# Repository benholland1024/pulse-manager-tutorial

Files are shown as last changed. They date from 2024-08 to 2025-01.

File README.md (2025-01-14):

<h1 align="center"> 🫀 Pulse Manager Tutorial</h1>

<h4 align="center">A description of how to recreate the hardware needed to use the <a href="https://github.com/benholland1024/pulse-manager">pulse-manager</a> software.</h4>

<br/><hr/><br/>

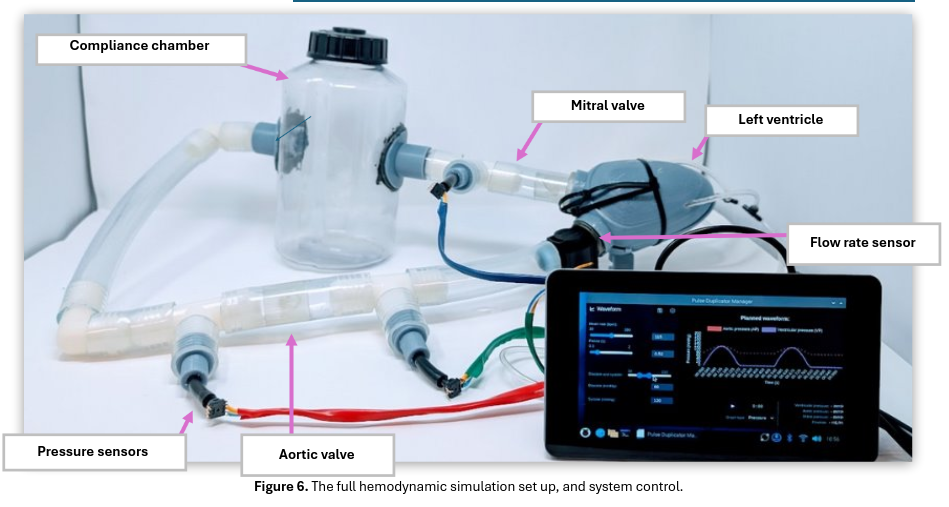
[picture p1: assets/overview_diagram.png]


<h2>Contents</h2>

 1. <a href="#supplies">**Required tools and supplies**</a>
 2. <a href="#cardiovascular-model">**The cardiovascular model**</a>
    - 2.1. Print the heart
    - 2.2. Print the heart casing
    - 2.3. Assemble compliance chamber
    - 2.4. Assemble tubing and sensors
 3. [**The air pump**](#air-pump)
    - 3.1. Create inflatable pockets
    - 3.2. Attach tubing to valves and air source
 4. [**The Raspberry Pi controller**](#rpi)
    - 4.1. Print case for RPi screen
    - 4.2. Set up RPi with a keyboard and mouse
    - 4.3. Set up the pulse-manager software
    - 4.4. Circuitry
 5. [**Testing**](#testing)
    - 5.1. Testing the screen interface

<br/><hr/><br/>

<h2 id="supplies">1. Required tools and supplies</h2>

The following tools were used:
 - An [Anycubic Photon Mono M5s](https://store.anycubic.com/products/photon-mono-m5s?srsltid=AfmBOoo6R4wCbVnCGKRZ7tQgiQt0xwVnhSDFUFg9_NGr83IOjvOBaMKt) 3d printer, and the slicer software
 - The [SolidWorks software](https://www.solidworks.com/), provided by the University of Akron, running on a Windows computer
 - A <a href="https://www.amazon.com/dp/B0067FFW6E">dental vacuum former</a>
 - A <a href="https://www.amazon.com/dp/B075L6K1KM">heat press</a>
 - A <a href="https://www.amazon.com/dp/B07RZV2DW8">soldering iron</a>
 - A <a href="https://www.amazon.com/dp/B07PPRDBM5">step drill bit</a> that goes up to 1.375 inch at least
 - A <a href="https://www.homedepot.com/p/310230031">drill press</a>
   - _Provided to us by the University of Akron. This must be big enough to fit the compliance chamber, ~13cm, plus the step bit_

The following supplies were used:
 - 3d printing supplies:
   - <a href="https://store.anycubic.com/products/high-speed-resin">Anycubic high speed resin</a>
   - <a href="https://www.amazon.com/dp/B08RWMMVCH">Superflex 80A printing resin</a>
   - <a href="https://www.amazon.com/dp/B08GJTGPYQ">Siraya Tech high-temp resin</a>
   - Isopropyl alcohol to clean the prints.
 - Electronics: 
   - An <a href="https://www.amazon.com/dp/B07PBF6DX5/">Endoscopic camera</a> (optional)
   - USB-c converter for RPi for camera (optional)
   - A <a href="https://www.amazon.com/dp/B0899VXM8F">Raspberry Pi</a> and its <a href="https://www.amazon.com/dp/B07TYQRXTK"> power supply</a>
   - A [microusb to HDMI socket](https://www.amazon.com/dp/B09LYPXPH6) converter, if using HDMI and a RPI 4 or 5
   - A [microsd card](https://www.amazon.com/dp/B0B7NXBM6P) for RPi memory.
   - A <a href="https://www.amazon.com/dp/B00GFAN498">Wifi USB dongle</a>for the Raspberry Pi (or ethernet)
   - A <a href="https://www.raspberrypi.com/products/raspberry-pi-touch-display/">touchscreen for the RPi</a>
     - _Or, a keyboard mouse and screen, if preferred._
   - An <a href="https://www.amazon.com/dp/B00NAY3RB2">analog to digital converter</a> circuit component
   - Three <a href="https://www.digikey.com/en/products/detail/sensata-crydom/CMX60D10/221843">Crydom</a> relays (CMX60D10)
   - Three <a href="https://www.mcmaster.com/2555N12/">solenoid valves</a> (Clippard, EV-P-10-25-A0-v)
   - A <a href="https://www.amazon.com/dp/B07QNN2GRV">flow meter</a> (Digiten)
   - Three <a href="https://www.digikey.com/en/products/detail/nxp-usa-inc./MPVZ5004GW7U/1168374">pressure sensors (MPVZ5004GW7U)</a>
   - A custom PCB from JCLPCB
   - A <a href="https://www.amazon.com/dp/B0852HX9HV/">12 volt power supply and its wire adapter</a>

   - Some <a href="https://www.amazon.com/dp/B01N0VNNKO">solder</a>
 - Tubing:
   - 10 ft of <a href="https://www.mcmaster.com/5233K72/">1 inch I.D. PVC tubing</a>
   - 10 ft of <a href="https://www.mcmaster.com/5233K56/">1/4 inch I.D. PVC tubing</a>
     - _to connect to the <a href="https://www.grainger.com/product/55NW90">pressurized air spigot</a> on our chem hood_
   - 10 ft of <a href="https://www.mcmaster.com/5233K404/">1/8 inch I.D. PVC tubing</a> for air valves + inflatable pockets
   - 10 ft of <a href="https://www.mcmaster.com/5233K415/">5mm I.D. PVC tubing</a> for connecting pressure sensors.
     - _We used some tubing we had, which I measure as about 5mm I.D. - it stretches over the pressure sensor, which is made for 5.59mm_
 - Tubing reducers:
   - 1 <a href="https://www.amazon.com/dp/B08JCCP63D">1/4 to 1/8 barbed tube reducer</a> for air supply
   - 3 5mm to 1/8 inch barbed tube reducer (this must be modelled + printed)
 - Other tubing connectors:
   - 2 <a href="https://www.mcmaster.com/5372K377/">1 inch elbow connectors</a>
   - 5ish <a href="https://www.mcmaster.com/5372K627/">1 inch T connectors</a>
   - 5 <a href="https://www.amazon.com/dp/B08JCS1W24">1/8 inch T connectors</a>
   - 6 <a href="https://www.mcmaster.com/5117K83/">1/8 inch barb to 10-32 threaded connectors</a> for air valves
   - 1 1 inch to 1 inch thread adapter (like <a href="https://www.amazon.com/dp/B0BQGJCCRP">this</a> but with 1" on both ends - I found it at home depot).
     - This is optional! Used with a <a href="https://www.amazon.com/Spears-PVC-THREADED-CAPS-1in/dp/B000VYJ4UC">1 inch plastic pvc cap</a> to make a removable entrance.
 - Inflatable pocket material
   - 80A shore polyether film, 0.012 inches in thickness from <a href="https://www.americanpolyfilm.com/polyether-tpu-film">American Polyfilm</a>
   - <a href="https://www.amazon.com/dp/">PVC adhesive</a> (maybe not necessary?)
 - Compliance chamber materials:
   - <a href="https://www.amazon.com/dp/B0006O1ICE">JB weld steel adhesive</a>
   - A disposable mixing dish and disposible brush (or popsicle stick) to apply the adhesive.
   - A <a href="https://www.mcmaster.com/3999T7/">clear jar</a> for the compliance chamber
   - Some <a href="https://www.amazon.com/dp/B0BXWJDBNS/">220 grit sandpaper</a>
 - Misc:
   - Zip ties, to seal the heart structure casing

While testing the system, the following was used:
 - Bread boards
 - Pin wires
 - LEDs
 - A multimeter

<br/><hr/><br/>

<h2 id="cardiovascular-model">2. The cardiovascular model</h2>
<h3 id="print-the-heart"> 2.1. Print the heart</h3>

The heart structure requirements:
 - It should be flexible, so it can be compressed to simulate systole.
 - It should have two openings, which can make watertight connections with the tubing. Barbs were used for this. Our tubing was 1.25" in O.D.
 - Optionally, it may have a smaller opening to accomodate the endoscopic camera. This also must be watertight when the camera is inserted. 
 - It should have a volume that approximates the volume of the left ventricle at diastole (~100mL). The volume of a cone was used to roughly estimate this.

The flexible heart Solidworks file is available for download [here](https://github.com/benholland1024/pulse-manager-tutorial/blob/main/heartStruct25mm.SLDPRT) and the STL [here](https://github.com/benholland1024/pulse-manager-tutorial/blob/main/assets/cardiovascular-model/heartStruct25mm.STL). The steps to create the model in Solidworks are:
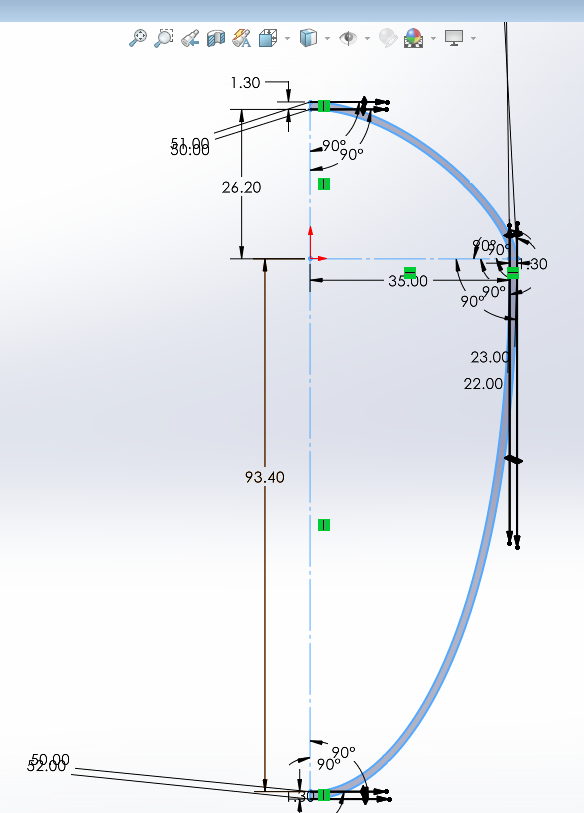
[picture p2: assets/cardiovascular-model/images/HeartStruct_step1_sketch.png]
 1. Sketch a cross section of half the heart structure wall (excluding the openings) with the desired volume. 
 2. Use the "revolve boss/base" tool around the y axis.
 3. Create a new reference plane from the "Top" plane, near where the holes will be made.
 4. Create another reference plane rotated about 30deg, which will be the angle of the holes.
 5. Sketch the outer diameter of the holes, I used 37.55mm. Extrude boss/base that sketch so it sticks out about 20mm.
 6. Sketch the inner diamter of the holes, 32.25mm (.5mm bigger than 1.25"). Make an extruded cut to create the holes.
 7. Create a plane perpendicular to the one last created.
 8. Switch the view to "hidden lines visible" and sketch a cross section of one of the barbs, which should be 0.5mm by 4mm.
 9. Create a different sketch on the same plane, and draw a line through the center of the cylinder.
 10. Revolve the barb around the center line to create one barb.
 11. Use linear pattern to create 3 more barbs, evenly spaced.
 12. Repeat steps 4-11 to create a second hole (or use the "mirror pattern" tool).

Save this file as a .STL, and import it into the AnyCubic Slicer software. 

Position it in the center of the print bed, on its side, with the holes facing the top and bottom. This minimizes the risk of suction cupping. 

Add supports using the "support only on platform" button. 

Click the "slice" button. Save the slice file to a flash drive to generate a .pm5 slice file. Print the model with <a href="https://www.amazon.com/dp/B08RWMMVCH">Superflex 80A printing resin</a>.

<br/>

<h3 id="print-the-casing"> 2.1. Print the heart casing</h3>

The heart structure casing requirements:
 - It should fit around the shape of the heart structure, with space for the uninflated inflatable pockets.
 - It should be rigid, so that the inflatable pockets inflate inward, squeezing the heart
 - It should have holes for the tubing of the inflatable pockets.
 - Optionally, it may have a hole for the endoscopic camera.
 - It should be printed in two halves which can be adhered together around the heart.

Below is a picture of the heart structure in the heart casing, with the inflatable pockets, to make the goal more clear. The heart casing halves are the blue solid structures:



The Solidworks and STL files for the heart casing halves are available here: 
[half1.sldprt](https://github.com/benholland1024/pulse-manager-tutorial/blob/main/assets/cardiovascular-model/PocketFrameHalf1.SLDPRT),
[half1.stl](https://github.com/benholland1024/pulse-manager-tutorial/blob/main/assets/cardiovascular-model/PocketFrameHalf1.STL)
[half2.sldprt](https://github.com/benholland1024/pulse-manager-tutorial/blob/main/assets/cardiovascular-model/PocketFrameHalf2.SLDPRT)
[half2.stl](https://github.com/benholland1024/pulse-manager-tutorial/blob/main/assets/cardiovascular-model/PocketFrameHalf2.STL)
They were made using similar methods to the heart structure model. The differences are:
 - The case halves are larger, which affects the first sketch and the sizes of the holes.
 - The case halves are halved, of course. This can be done by only rotating the initial sketch 180deg. 
 - They have holes for the inflatable pockets, made via vertical extruded cuts, repeated via the radial pattern tool. 
 - Optionally, they have holes for the endoscopic camera. 
 - Optionally, they have snap-fit joints to adhere the two halves. I couldn't get these to work, and used zip ties instead. 

Export these files, add supports in the slicer, and save it. Print these with <a href="https://store.anycubic.com/products/high-speed-resin">Anycubic high speed resin</a>, OR using <a href="https://www.amazon.com/dp/B0C8NTLYKB">Anycubic high clear resin</a> if you want to see the liquid inside the frame. The high clear resin is harder to print with, requiring ~8 seconds per layer.

<br/>

<h3 id="compliance-chamber"> 2.3. Assemble compliance chamber</h3>

The compliance chamber requirements:
 - It must be a clear chamber, so the water level can be determined.
 - It must have two holes, each with an airtight connection to the large tubing.
 - It must be both air and water tight, both at the holes and at the top opening.

Two connectors must be printed - see the files [ComplianceConnector.sldprt](https://github.com/benholland1024/pulse-manager-tutorial/blob/main/assets/cardiovascular-model/ComplianceConnector_25mm.SLDPRT) and [ComplianceConnector.stl](https://github.com/benholland1024/pulse-manager-tutorial/blob/main/assets/cardiovascular-model/ComplianceConnector_25mm.STL).  These act as gaskets.  The inner diameter of these is 31.8mm, with 0.5mm barbs, to fit the 1.25 inch (31.75mm) tubing. The outer diameter is 34.94mm, to fit into the hole we'll drill, which will be 1.375 inches (34.925mm) in diameter. Also note that the flat surface is curved to fit around the radius of the clear jar, which is 125mm in diameter. 

Print two of these using the [high speed resin](https://store.anycubic.com/products/high-speed-resin). Once printed, ensure they can snugly hold the tubing. 

Use the step drill bit to drill two 1.375 inch holes into the [clear jar](https://www.mcmaster.com/3999T7/), on opposite sides, about halfway up. 

Insert the connectors into the holes, making sure they fit snugly against the side of the jar. 

Use the 220 grit sandpaper to smooth the jar around both holes, where the connector will be placed. Then, use 220 grit sandpaper to smooth the connector, on the surface that will touch the jar. Make sure these surfaces are smooth. Then clean these surfaces with isopropyl alcohol and water, and let them dry.

Using gloves, a disposable dish, and a popsicle stick (or some disposable brush), mix the [JB Weld Steel Adhesive](https://www.amazon.com/dp/B0006O1ICE) properly and paint a semi-thick coat evenly on the connectors, where they'll meet the jar. 

Balance the jar on one of the connectors, and place something heavy on the other connector, to let the adhesive cure. Below is a picture of the compliance chamber curing. 



Leave the compliance chamber like this for 24 hours. Then, check to make sure the chamber is waterproof. 

<br/>

<h3 id="tubing-and-sensors"> 2.4. Assemble tubing and sensors</h3>

The tubing assembly requirements:
 - Tubing must connect the heart structure and compliance chamber, in a loop.
 - Artificial aortic and mitral valves must be placed in the appropriate places.
 - 3 pressure sensors must be placed in the appropriate places.
 - A flow sensor must be placed in the appropriate place.
 - The entire cardiovascular loop must be watertight.
 - The tension from the tubing must not damage the heart structure!

The appropriate places for the valves and sensors can be seen on the diagram below, from [this paper by Rodriguez](https://www.semanticscholar.org/paper/Redesign-and-performance-evaluation-of-a-cardiac-Rodriguez/98711b67d424e339e281634dccae912807a91a78).

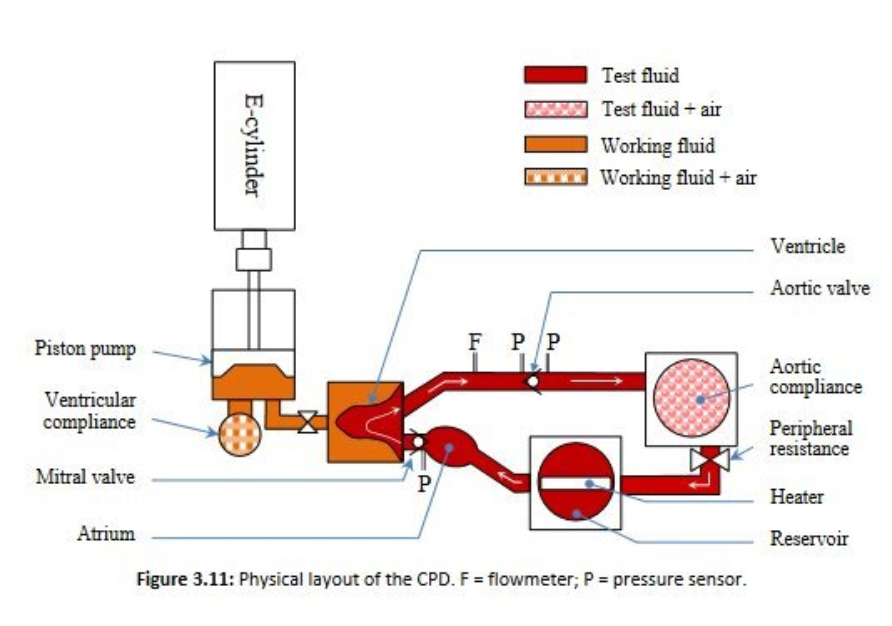
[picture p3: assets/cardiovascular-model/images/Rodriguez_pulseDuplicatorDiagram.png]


The complete set up uses 1" I.D. tubing, 90 degree connectors, T connectors, 3d printed reducer connectors, smaller tubing, the pressure sensors, and the flow rate sensor. A picture of the set up is shown below. 

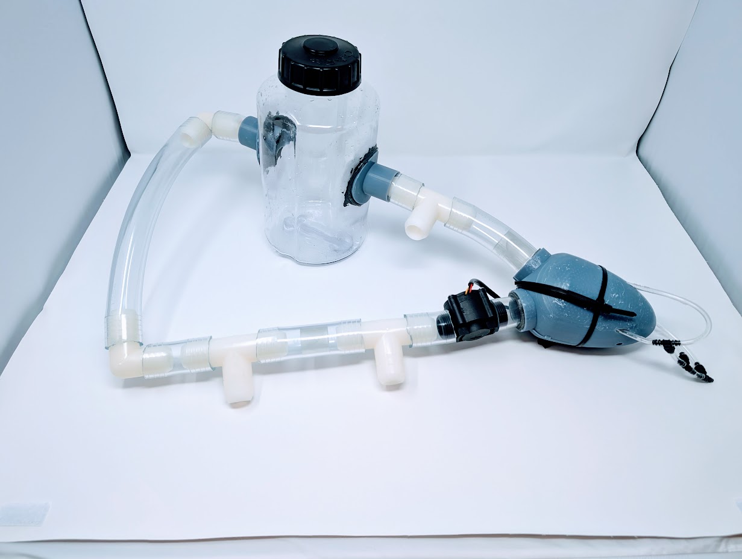
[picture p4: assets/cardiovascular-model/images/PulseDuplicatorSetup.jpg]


<br/><hr/><br/>

<h2 id="air-pump">3. The air pump</h2>

<h3 id="inflatable-pockets"> 3.1. Create inflatable pockets</h3>

The infatable pocket requirements:
 - These must be hollow, inflatable, and airtight.
 - These must be in a shape compatible with the heart structure.
 - These must have tubes connected to them, for inflation.

The idea for inflatable pockets was taken directly from [this paper](https://www.science.org/doi/full/10.1126/scirobotics.ade2184) by Goswami. 

First, two negative mold halves must be modeled and printed. Here are some general steps for modeling these in Solidworks:
 1. Start by modeling the pocket shape.
    - The pocket should wrap 80 degrees around the heart structure, and the inner face should press the structure inward. Reference pictures can be found in Dr. Goswami's paper.
    - Sketch a cross section of the pocket and revolve boss/base it 80 degrees.
    - This file is available here: [inflatable_pockets.sldprt](https://github.com/benholland1024/pulse-manager-tutorial/blob/main/assets/air-pump/inflatable_pockets.SLDPRT). There's no need to print this.
 2. Create a new assembly from the inflatable pocket model.
 3. In that assembly, create two new parts, both rectangular prisms. These will be the mold halves, and should be of dimensions that cover the inflatable pocket model.
    - Use mates to push the two halves together, and position them on top of the pocket model.
    - Edit one of the halves in the assembly (right click on it, click "edit part").
    - On the top bar, click "Insert → Features → Cavity". Click the intersecting pocket part. Adjust the parts if needed.
    - Repeat this procedure on the second half.
 4. Save the two negative parts. You can find these files here:
[negative1.sldprt](https://github.com/benholland1024/pulse-manager-tutorial/blob/main/assets/air-pump/inflatable_pockets_negative1.SLDPRT)
[negative1.stl](https://github.com/benholland1024/pulse-manager-tutorial/blob/main/assets/air-pump/inflatable_pockets_negative1.STL)
[negative2.sldprt](https://github.com/benholland1024/pulse-manager-tutorial/blob/main/assets/air-pump/inflatable_pockets_negative2.SLDPRT)
[negative2.stl](https://github.com/benholland1024/pulse-manager-tutorial/blob/main/assets/air-pump/inflatable_pockets_negative2.STL)
    - The [assembly file](https://github.com/benholland1024/pulse-manager-tutorial/blob/main/assets/air-pump/mould_maker.SLDASM) is also available if you're curious.
 5. **NOTE:** I forgot to add some small air holes in these molds! You should edit these parts to do that, so the vacuum former will work better. I added these holes with a drill afterwards, which cracked the molds and required using resin to fix.
   
Print the two negative mold STLs using <a href="https://www.amazon.com/dp/B08GJTGPYQ">Siraya Tech high-temp resin</a>. This resin is hard to print with -- if you're printing at room temperature, print with 90 seconds per bottom layer, 6 bottom layers, and 18 seconds per regular layer. 

Once you have the two negative molds, get the 80A polyethylene film from <a href="https://www.americanpolyfilm.com/polyether-tpu-film">American Polyfilm</a> and cut squares that are the right size for the <a href="https://www.amazon.com/dp/B0067FFW6E">dental vacuum former</a>.  Place the first mold in the former, load the film (I used 2 sheets at once), heat it for ~2 minutes, then switch to the vacuum to create the shape of half a pocket. **NOTE**: This is where the holes in the molds matter. Carefully extract the pocket half, removing the ball bearings. Repeat that procedure with the other negative mold.

You should now have two halves of a pocket. Put these halves back in the molds and push them together. Cut off any excess film -- this film will melt if it touches the heat press, causing toxic fumes and a mess of melted plastic. Place the two molds into the <a href="https://www.amazon.com/dp/B075L6K1KM">heat press</a> and heat it to 160 degrees C. Sandwich the heat press, and leave it there for 15 minutes or so before turning the heat press off. Once cool, take out the pocket, and check whether it's airtight. 

Finally, cut a length of 1/8" I.D. tubing (5-10cm). Cut a hole in the convex side of the pocket and insert the tube, ensuring it's positioned correctly to fit in the heart structure casing. Glue the tube in place -- I first used <a href="https://www.amazon.com/dp/">PVC adhesive</a>, and once dry, painted some of the <a href="https://www.amazon.com/dp/B08RWMMVCH">Superflex 80A printing resin</a> onto the pockets and cured them. I'm not sure if the PVC adhesive is necessary.

Blow into the tubing to check if the pockets are airtight. Getting these airtight was hard and seemed to require a bit of luck, and several rounds of the Superflex resin.

Create 4 pockets this way. The same 2 negative mold halves can be reused, of course. 

The final product is pictured below, placed in the heart structure casing.

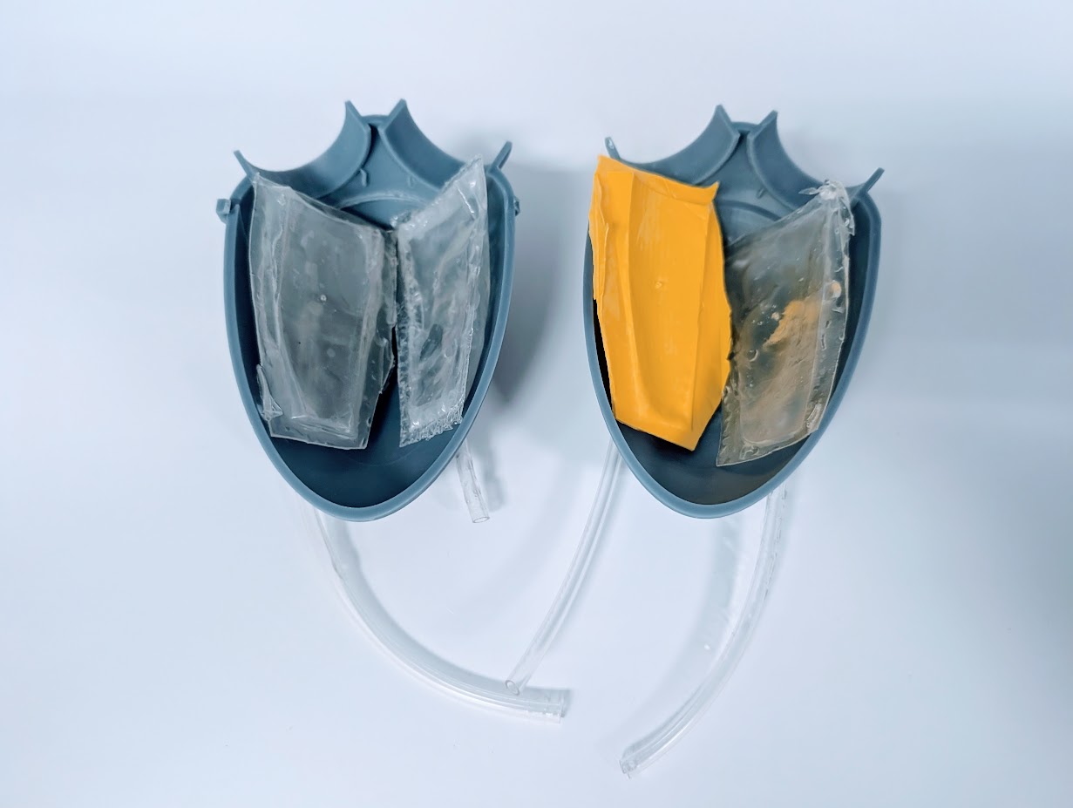
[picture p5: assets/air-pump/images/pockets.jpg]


<br/>

<h3 id="air-source"> 3.2. Attach tubing to valves and air source</h3>

The picture below shows the set up for the air tubing. _(This picture shows an earlier version of the heart structure casing -- ignore that.)_ 

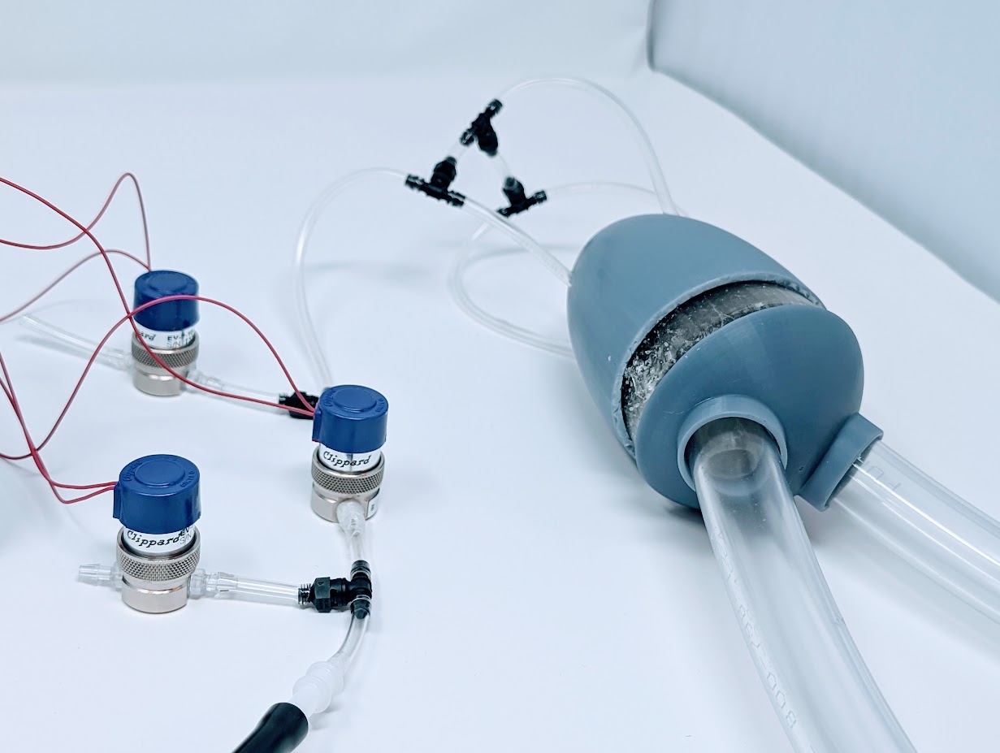
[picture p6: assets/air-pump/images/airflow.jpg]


Note that the black tubing shown in the bottom attaches to a source of compressed air. 

Also note that two of the air valves release the air to the atmosphere. This prevents pressure build up, which can disconnect the tubing. 

<br/><hr/><br/>

<h2 id="rpi">4. The Raspberry Pi controller</h2>

<h3 id="rpi-case"> 4.1. Print case for RPi screen</h3>

In retrospect, I'm not sure if the <a href="https://www.raspberrypi.com/products/raspberry-pi-touch-display/">touchscreen</a> was the best choice. It could be replaced with a monitor, keyboard and mouse for easier control and a larger screen - although it would then take up more space. 

If you're using the touch screen, you should print a display case. I found basic models [here](https://www.printables.com/model/18153-raspberry-pi-7-inch-touchscreen-display-case/files), and also used [this deep version](https://www.printables.com/model/151799-raspberry-pi-deep-7-inch-touchscreen-display-case) of the case. 

Ultimately, I plan to create a custom case based on the ones above, that can accomodate the added sensors.  My plan is shown in the image below.

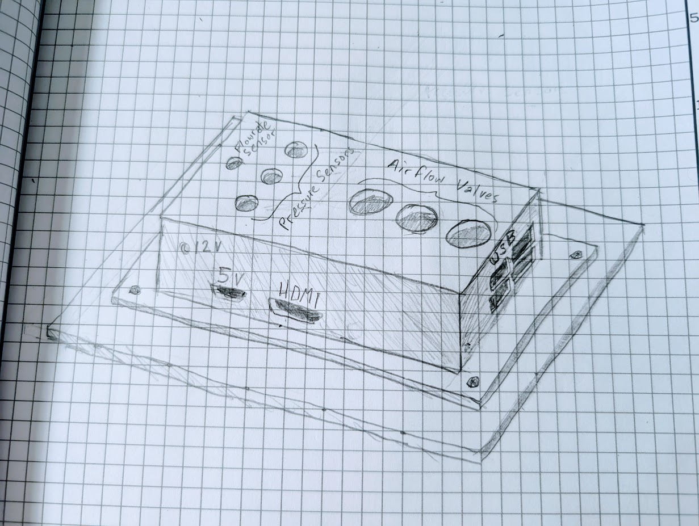
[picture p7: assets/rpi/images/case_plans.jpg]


<br/>

<h3 id="rpi-setup"> 4.2. Set up RPi with a keyboard and mouse</h3>

Get the microsd card and plug it into a computer (not the RPi, yet). [Install the Raspberry Pi OS](https://projects.raspberrypi.org/en/projects/raspberry-pi-setting-up/2) onto the SD card. 

Now plug the SD card into the RPi. Plug the RPi into power. Follow the instructions to plug in the touchscreen, and/or use HDMI to display the RPi on a screen, and connect a mouse and keyboard. 

The computer should boot up! If you're using the touchscreen, the screen is likely upside down compared to what you want -- click the RPi menu icon, then "Preferences → Screen Configuration". Right click the touch screen and click "Orientation → Inverted", then click "apply" and "ok". 

Next I like to go to "Preferences → Appearance Settings", then the "Taskbar" tab, and make the position on the bottom. You can set the taskbar "location" here too, if using two screens. Then in the System tab, I set the theme to dark. 

The keyboard may need configured to US instead of British (or else you may get a £ when you want a $, among other issues.) Open a command line and type `sudo raspi-config`.  In "localisation options", update both the keyboard and timezone. This info came from [here](https://forums.raspberrypi.com/viewtopic.php?t=69752). The displayed clock still might not work, which is acceptable to me. 

You must enable SPI as well. Enter `sudo raspi-config`, go to "Interface Options", "SPI", then hit "Yes" to enable.

You'll need to connect to wifi, using the wifi usb dongle (or ethernet). If you're a U of Akron student, there's a guide to connecting to Eduroam on Linux [here](https://www.uakron.edu/it/connecting-to-the-network.dot). 

<br/>

<h3 id="software"> 4.3. Set up the pulse-manager software</h3>

Now we can install the software. Open up a command line. You'll need the `git` command, which should be installed. Enter `git -v` to make sure you don't get an error. Install the [pulse-manager repo](https://github.com/benholland1024/pulse-manager) wherever you'd like.  These commands are what I use:

```bash
mkdir github
cd github/
git clone https://github.com/benholland1024/pulse-manager.git
cd pulse-manager/
```

The software uses Python, so make sure you have that installed by running `python -version` and ensuring there's no error.  
Python needs some packages installed. Install them by running: 

```bash
sudo pip install -r requirements.txt --break-system-packages
```

To edit the software, open the main menu, then click "Programming → Geany". On the top menu bar, click "Project → New...". Enter the following, replacing "benholland" with your username:

| Prompt     | What to write                          |
|------------|----------------------------------------|
| Name:      | pulse-manager                          |
| Filename:  | /home/benholland/pulse-manager         |
| Base path: | /home/benholland/github/pulse-manager/ |

Click "create". Now click "Tools → Plugin Manager", check "File Browser", and click "close". Now at the top of the panel on the left, click the right arrow button until the word "Files" is highlighted -- you should see all the files in the project! 

Click "Document → Indent Type → Spaces" and "Document → Indent Width → 2". 

_(I know this set up is a pain but you only have to do it once, and Geany is pretty good otherwise.)_

In the bottom panel of Geany, click the down arrow until it says "terminal".  Type "pwd" to make sure you're in the `pulse-duplicator` project folder. (Navigate there using `cd` if not). 

Now, you should be able to run the app! Try this: 

```bash
python app.py
```

If you get an [error about edge detection](), you may need to run these two commands:
```bash
sudo apt remove python3-rpi.gpio
sudo apt install python3-rpi-lgpio
```
Then try `python app.py` again. 

If the window opens but says "Error: 404", open `app.py` and ensure the line which includes `eel.init(os.path.abspath` has the correct file path for the project. 

<br/>

With the app working, you can make a shortcut to open the app. Create a new file.

```bash
nano ~/Desktop/pulse-manager.sh
```

Now add this text:
```bash
#!/bin/bash
/home/benholland/github/pulse-manager/app.py
```

Save the file (ctrl-x, "y"). Now make it executable:

```bash
chmod +x pulse-manager.sh
```

Now you can double click this file to start the app!

<br/>

<h3 id="circuitry"> 4.4. Circuitry</h3>

The RPi needs to have its pins attached correctly to the sensors and solenoid valves. 

I first did this using breadboards and pin connectors. I recommend using these tools if any modifications are being made.

Once the breadboard system was working, I used the free software [KiCad](https://www.kicad.org/) to create a circuit schematic -- see the first image below.  Then a PCB design was created from that schematic, see the second picture.  

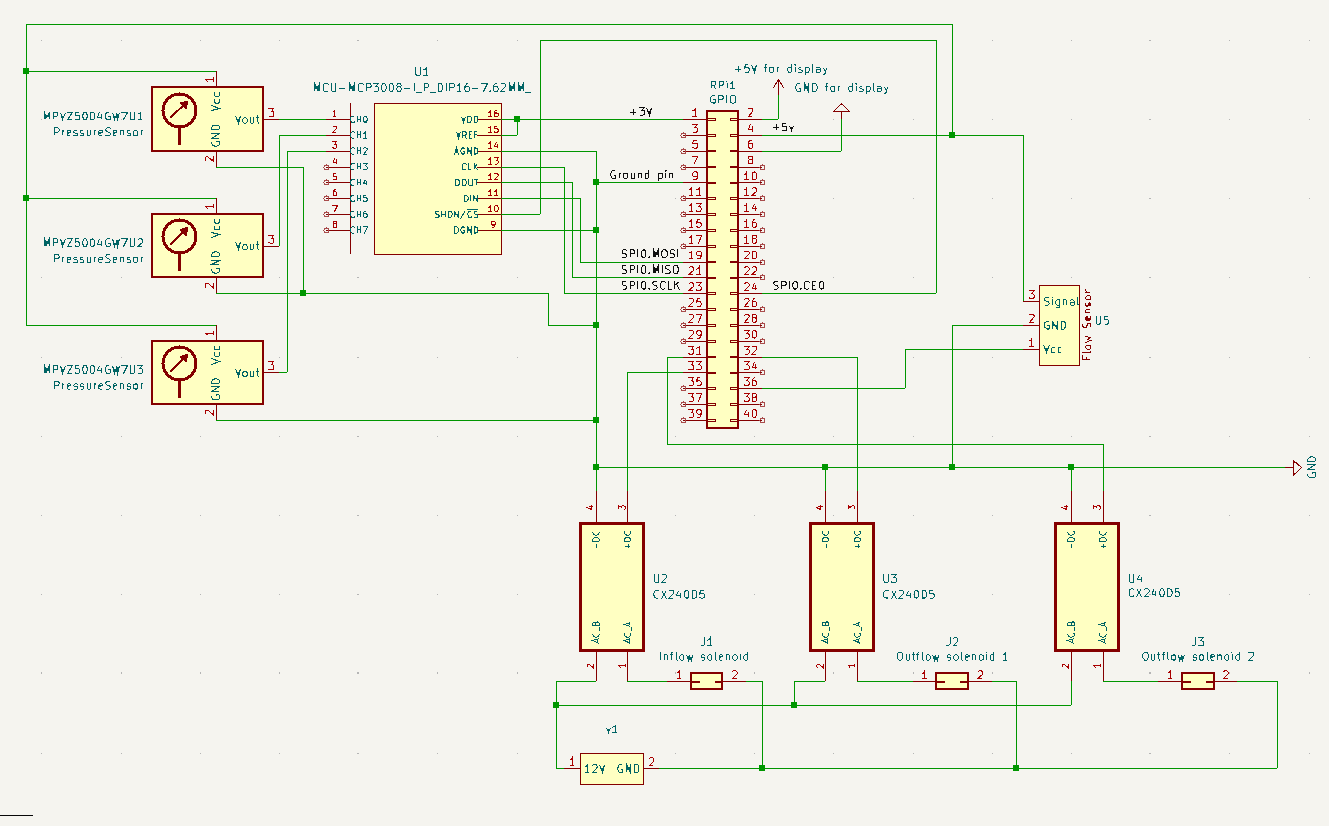
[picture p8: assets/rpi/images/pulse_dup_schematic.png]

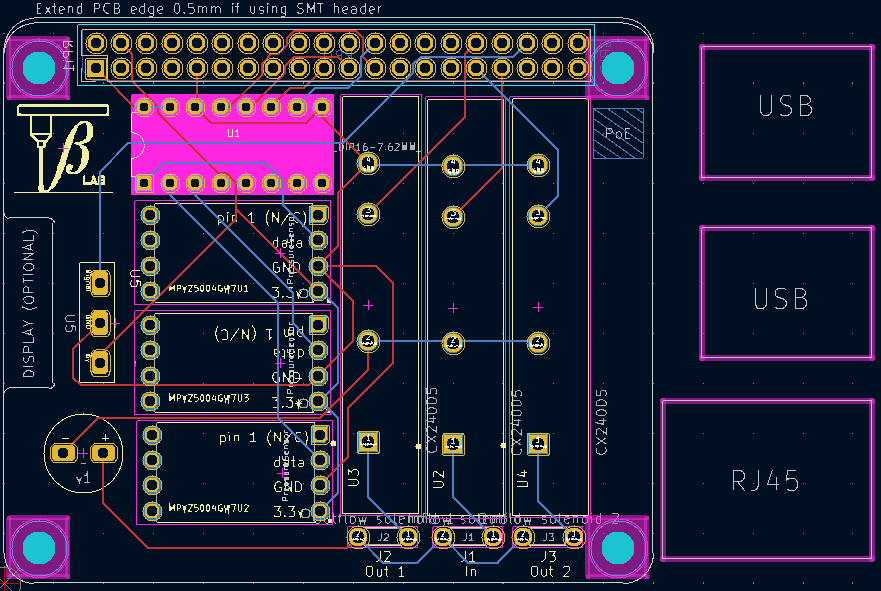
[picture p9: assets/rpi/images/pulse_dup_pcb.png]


The files for these schematics are available [here](https://github.com/benholland1024/pulse-manager-tutorial/blob/main/assets/rpi/pulse_duplicator_circuit_files.zip).  Download that zip file and extract it.  The files should open in KiCad.

You'll need to order the PCB. I used the company [JLCPCB](https://jlcpcb.com/). In that zip file, there's another zip file called "gerber.zip".  You can upload that to the JLCPCB website to order the pcb.  

Or, if you change the PCB, follow [this](https://jlcpcb.com/help/article/how-to-generate-gerber-and-drill-files-in-kicad-7) to create a new gerber zip file, to be ordered.

<br/><hr/><br/>

<h2 id="testing">5. Testing</h2>

<br/> 

<h3 id="test-the-screen"> 5.1. Testing the screen interface</h3>

<br/><br/><br/><br/>

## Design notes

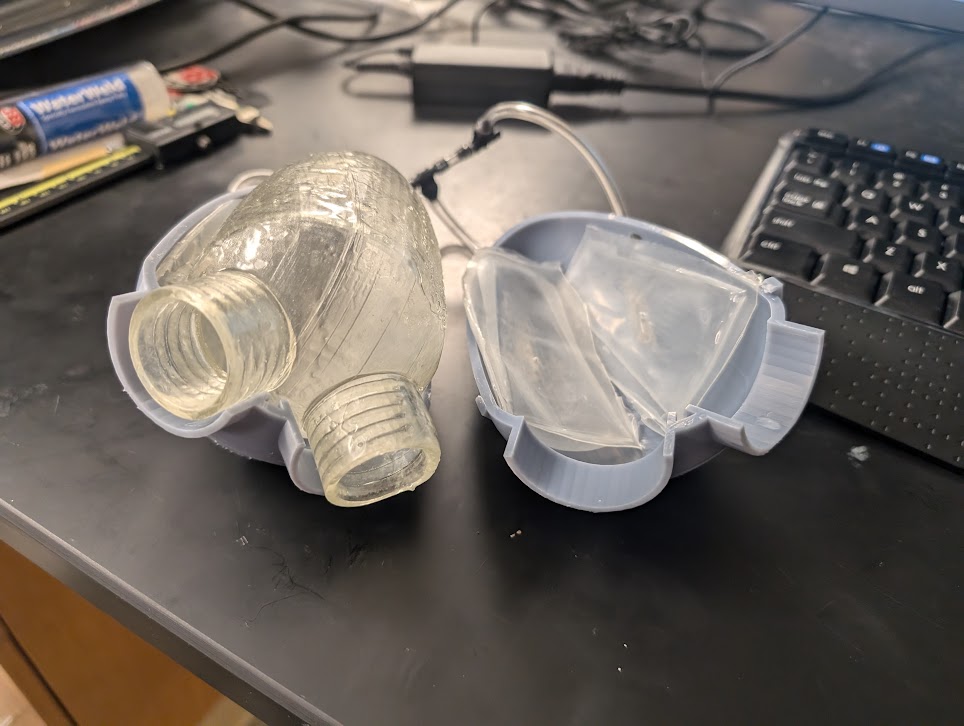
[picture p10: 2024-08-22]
assets/cardiovascular-model/images/heart_structure_in_casing.jpg

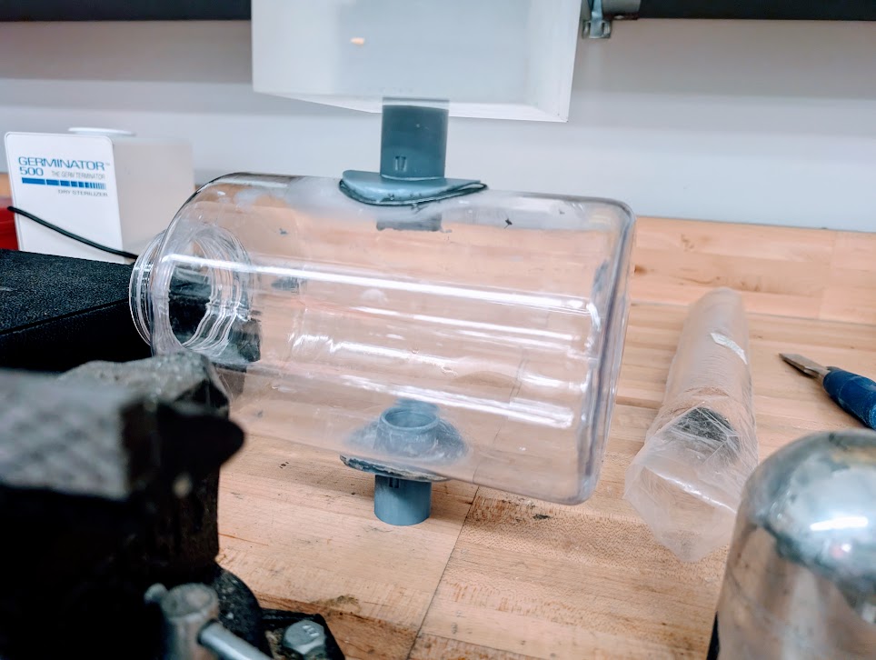
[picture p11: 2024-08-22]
assets/cardiovascular-model/images/compliance_chamber_curing.jpg

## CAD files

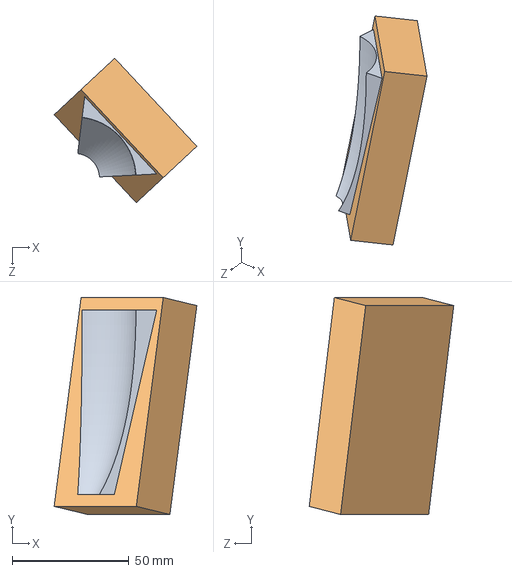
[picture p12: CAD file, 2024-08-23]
assets/air-pump/mould_maker.SLDASM
61.1 x 93.0 x 61.9 mm
inflatable_pockets_negative1
inflatable_pockets

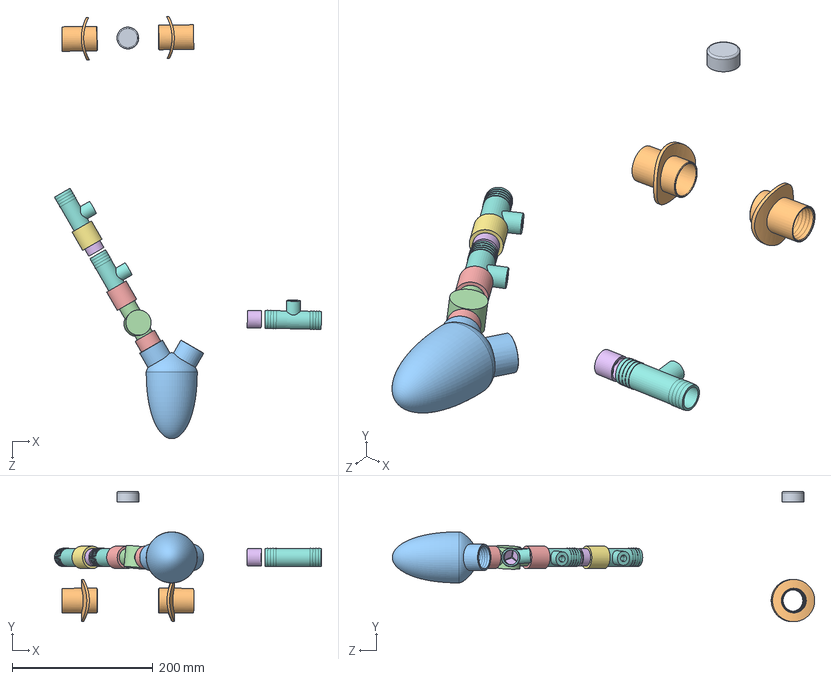
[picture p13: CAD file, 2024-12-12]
assets/tavr/TAVRassembly.SLDASM
379.3 x 185.1 x 600.2 mm
TeeAdapter9.5outer_To25inner x 3
less_short_25mm_tubing
Basic_Valve x 2
short_25mm_tubing x 2
flow_meter
heartStruct25mm
ComplianceConnector_25mm x 2
compliance chamber lid

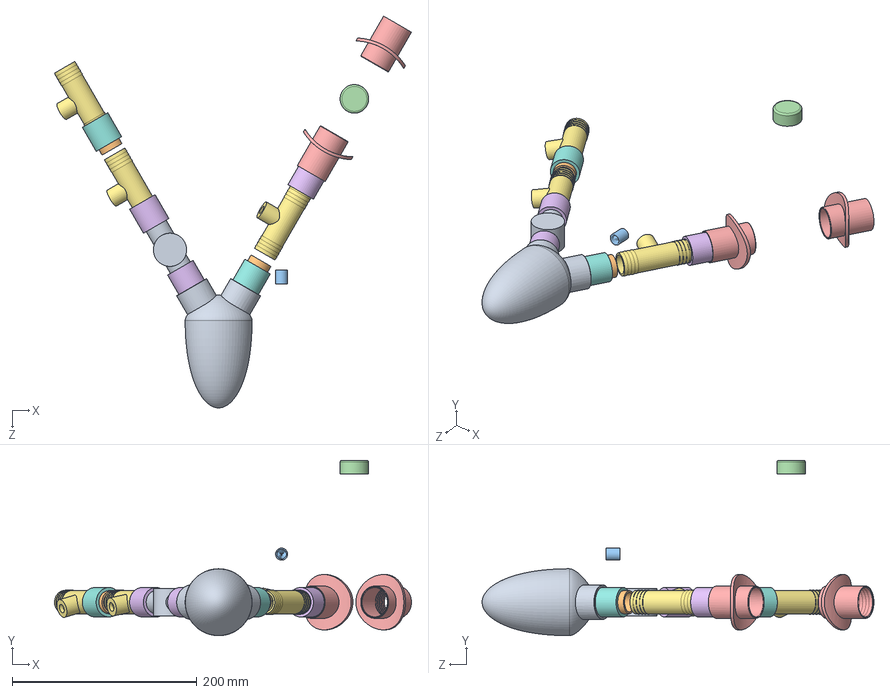
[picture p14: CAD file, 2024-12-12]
assets/tavr/nonTAVRassembly.SLDASM
386.9 x 190.1 x 424.6 mm
heartStruct25mm
less_short_25mm_tubing x 2
TeeAdapter9.5outer_To25inner x 3
short_25mm_tubing x 3
ComplianceConnector_25mm x 2
compliance chamber lid
Valve
Basic_Valve x 2
flow_meter

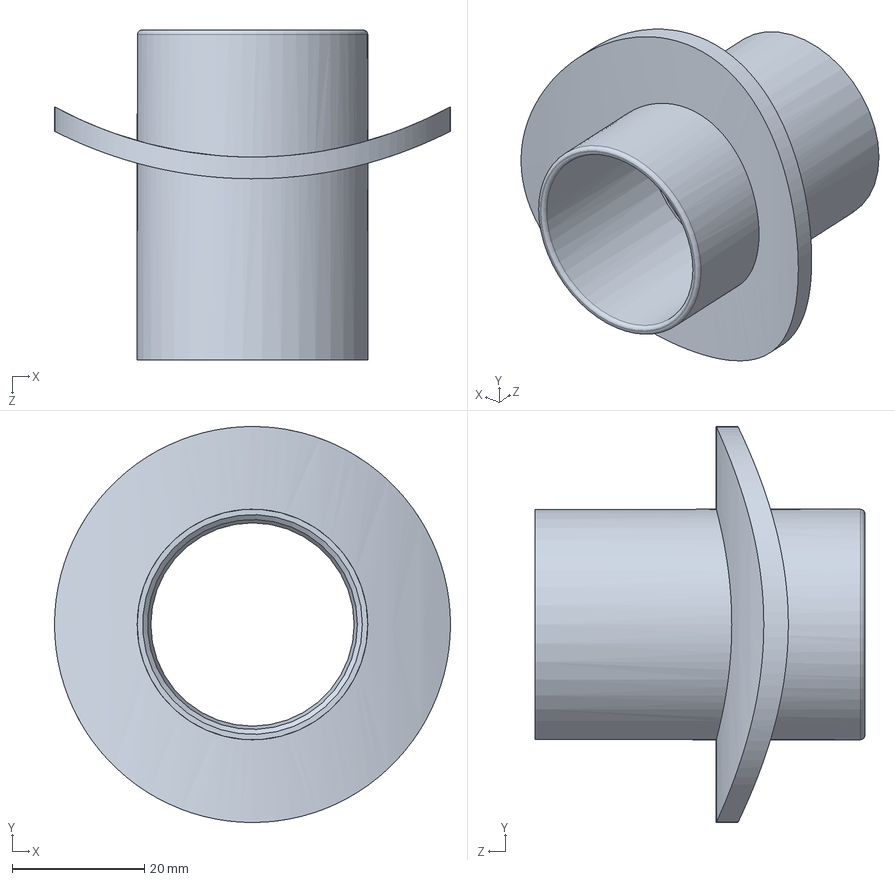
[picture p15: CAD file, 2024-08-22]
assets/cardiovascular-model/ComplianceConnector_25mm.SLDPRT
60.0 x 60.0 x 50.0 mm

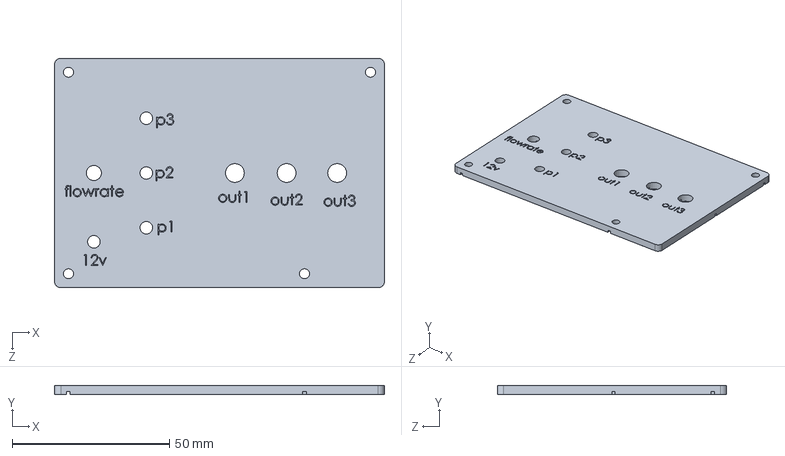
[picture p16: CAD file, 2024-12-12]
assets/tavr/rpi_custom_case_lid.SLDPRT
105.0 x 3.00 x 73.0 mm

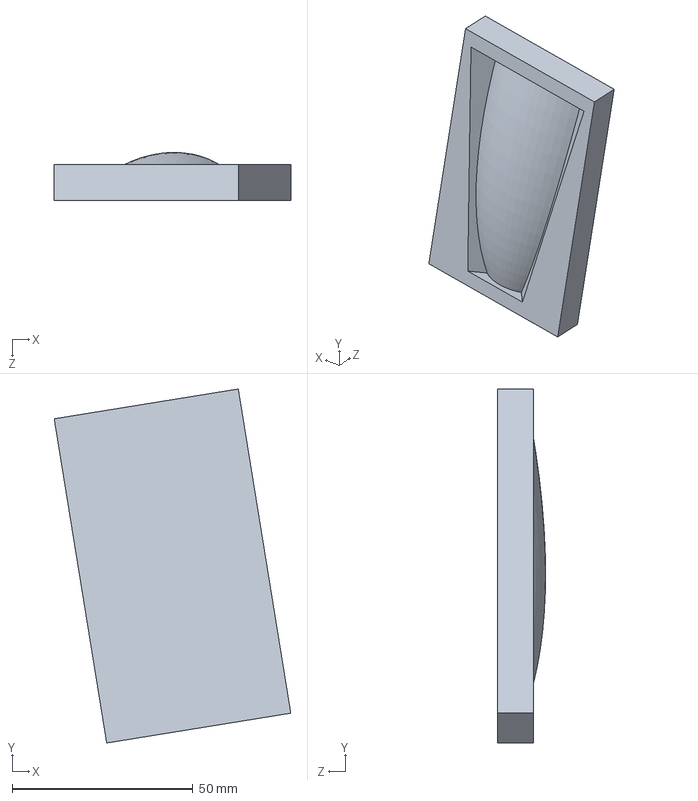
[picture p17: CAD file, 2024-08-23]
assets/air-pump/inflatable_pockets_negative2.SLDPRT
65.5 x 98.0 x 13.3 mm

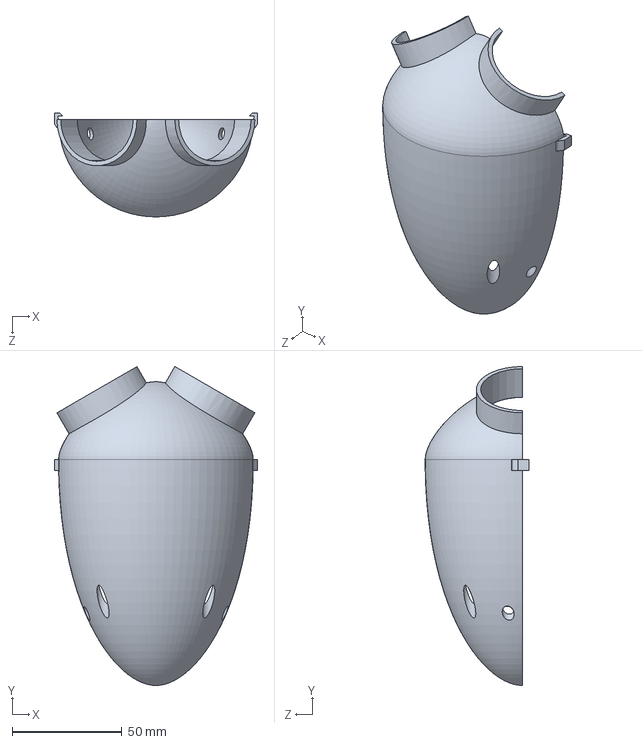
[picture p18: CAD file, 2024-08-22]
assets/cardiovascular-model/PocketFrameHalf1.SLDPRT
92.5 x 145.1 x 47.2 mm

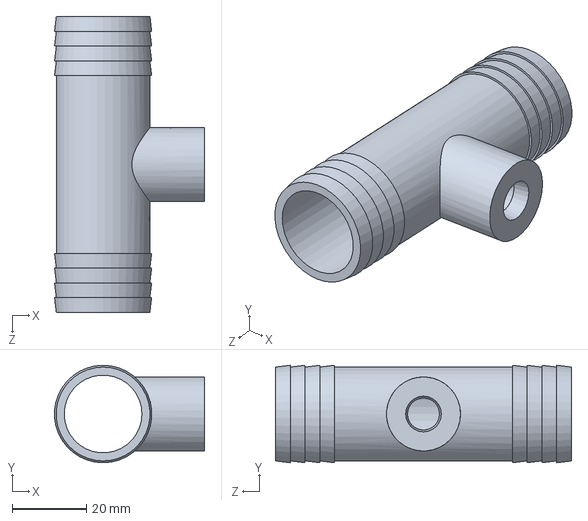
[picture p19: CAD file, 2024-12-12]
assets/tavr/TeeAdapter9.5outer_To25inner.SLDPRT
40.5 x 26.4 x 80.0 mm

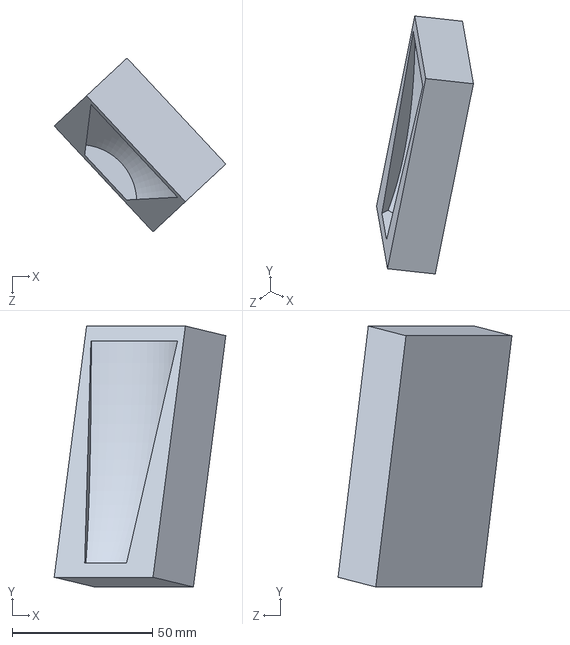
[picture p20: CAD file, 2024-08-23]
assets/air-pump/inflatable_pockets_negative1.SLDPRT
61.1 x 93.0 x 61.9 mm

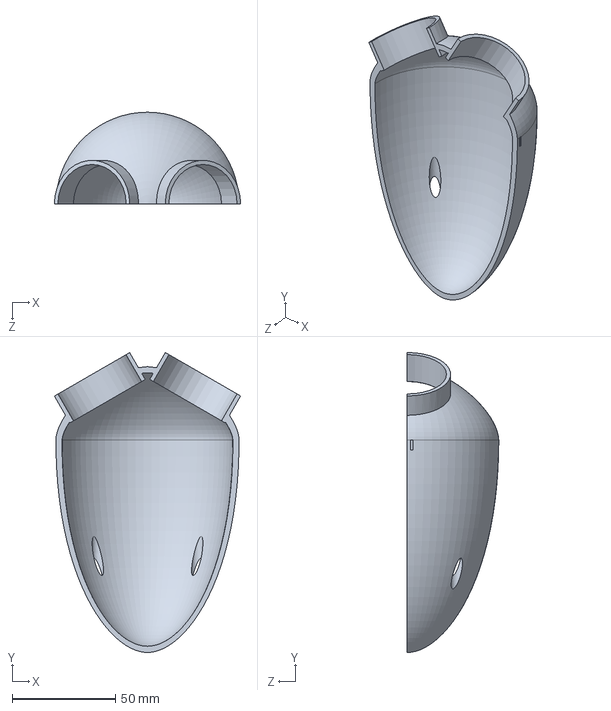
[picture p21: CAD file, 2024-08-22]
assets/cardiovascular-model/PocketFrameHalf2.SLDPRT
90.1 x 145.1 x 44.3 mm

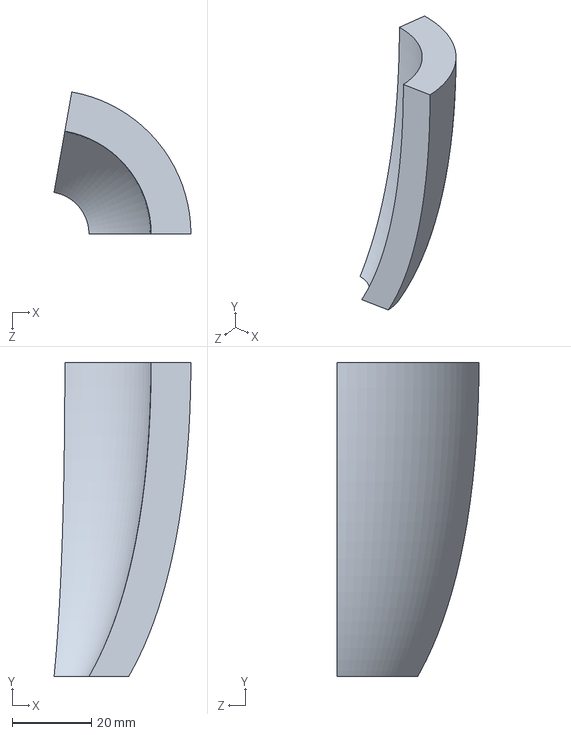
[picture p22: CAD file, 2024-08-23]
assets/air-pump/inflatable_pockets.SLDPRT
34.5 x 79.0 x 35.7 mm

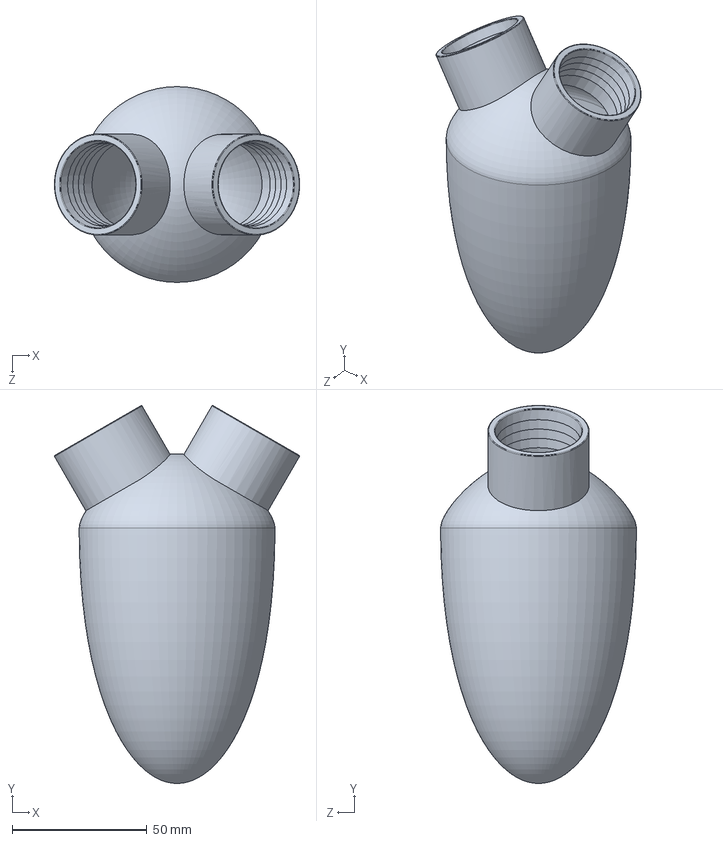
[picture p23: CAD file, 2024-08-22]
assets/cardiovascular-model/heartStruct25mm.SLDPRT
90.9 x 140.1 x 72.6 mm

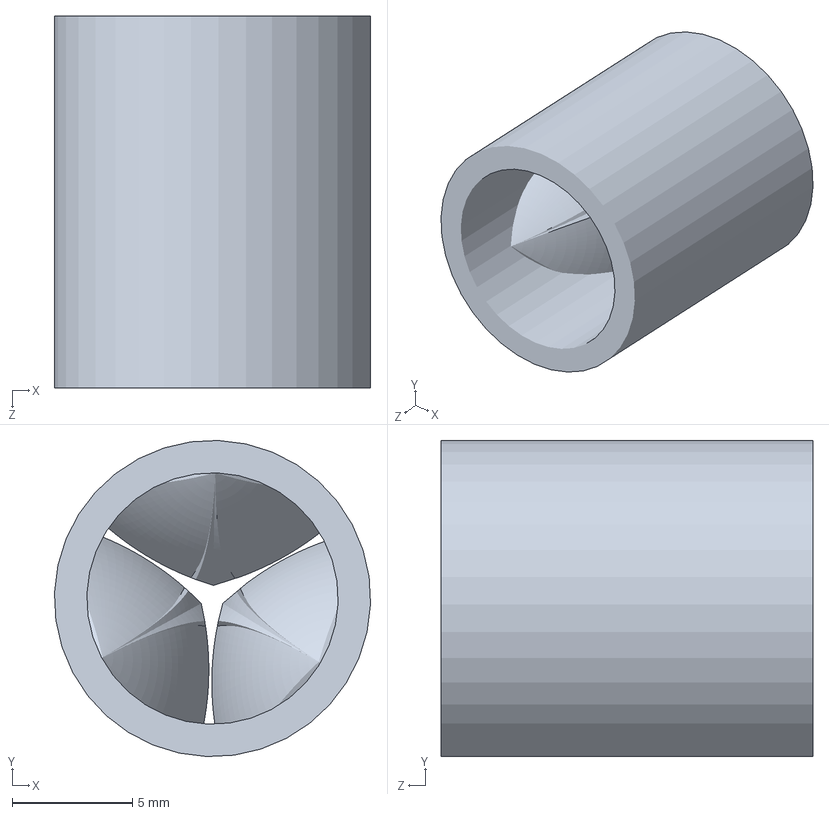
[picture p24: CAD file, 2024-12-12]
assets/tavr/Valve.SLDPRT
13.1 x 13.1 x 15.5 mm

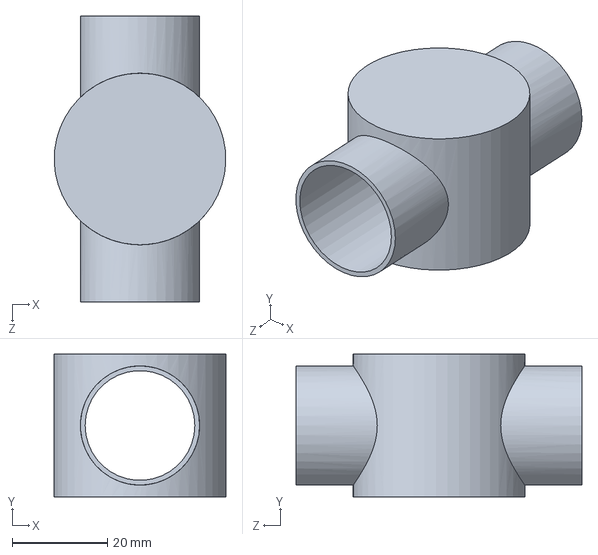
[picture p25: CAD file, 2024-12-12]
assets/tavr/flow_meter.SLDPRT
36.0 x 30.0 x 60.0 mm

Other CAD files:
assets/tavr/less_short_25mm_tubing.SLDPRT
assets/tavr/compliance chamber lid.SLDPRT
assets/tavr/short_25mm_tubing.SLDPRT
assets/tavr/Basic_Valve.SLDPRT
assets/air-pump/inflatable_pockets_negative1.STL
assets/air-pump/inflatable_pockets_negative2.STL
assets/cardiovascular-model/ComplianceConnector_25mm.STL
assets/cardiovascular-model/PocketFrameHalf1.STL
assets/cardiovascular-model/PocketFrameHalf2.STL
assets/cardiovascular-model/heartStruct25mm.STL
assets/tavr/compliance chamber.SLDPRT
assets/tavr/pressure_sensor.SLDPRT
